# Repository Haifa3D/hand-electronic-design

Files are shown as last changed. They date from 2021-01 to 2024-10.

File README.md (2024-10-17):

# Oded Hand Electrical Design  

This project is a sub-project of Haifa3D Robotic Hand.
In this project, we present the electrical design of the Oded Hand – a 3D printed robotic hand with five micro-DC motors. 
The aim of this design is to be low cost, accessible, easy to assemble, robust and lightweight.  

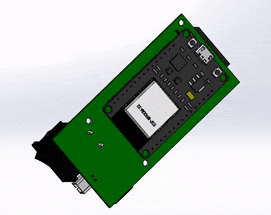
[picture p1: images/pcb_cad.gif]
   hand_gif  

## Design Description  
The Oded Hand can perform a variety of user-defined hand configurations using an autonomous adaptive grip along with a variety of configurable grip force levels.
The electrical design consists of four fingers with four different tendon-driven mechanisms actuated by four micro-DC motors, a passive thumb which magnetically locks in two discrete positions and wrist rotation driven by planetary gears and a DC motor. 

The electronic system consists of:
* The circuit and controller code
* The circuit housing and socket
* The batteries housing

The electronic system presented here also allows a Bluetooth communication between the Hand and your phone for settings configuration and a modular sensors control (see our [Mobile App](https://github.com/Haifa3D/haifa3d-hand-app)). For more details on how to manufacture and assemble the hand, please check out our [Mechanical Design](https://github.com/Haifa3D/hand-mechanical-design). 

## Who can benefit from this Design?  
The design is suitable for users with transradial amputation (below the elbow).
We welcome any new developers to enhance our design or to use the Oded Hand as a simulator for your new sensors/algorithms/methods that would potentially help users with controling their prosthetic hand.

## Design Files and Versions  
The STL files for the battery housing and the circuit housing can be found [here](CAD_files). The gerber files of the PCB design can be found [here](gerber_files/CAMOutputs) as well as the [schematic and layout](docs). The EAGLE files for modifying the board can be found [here](EAGLE_files). The Arduino code for the controller can be downloaded from [here](controller_software/Oded_Hand_board7_app2_4_6).

## Getting Started:
To build the electronic system for Oded Hand you will need a basic knowledge of soldering and the following componenets: 

| Component Name | Quantity | Value | links |
| --- | --- | --- | --- |
| ESP32 DEVKIT V1| 1 | - | [pinouts](https://randomnerdtutorials.com/esp32-pinout-reference-gpios/) [aliexpress](https://www.aliexpress.com/item/4000071762309.html?spm=a2g0s.9042311.0.0.64074c4du1Hh8a) |
| DRV8833 Pololu breakout board | 3 | - | [pololu](https://www.pololu.com/product/2130) | 
| micro metal dc motor | 5 | MP/LP, 100-200 RPM x 4, 30RPM x 1 | [pololu](https://www.pololu.com/product/2360), [aliexpress](https://www.aliexpress.com/item/1005003482247510.html?spm=a2g0o.productlist.main.5.70497ad7QQdXAy&algo_pvid=51493eeb-ec56-46bd-8e1c-2290c1519572&algo_exp_id=51493eeb-ec56-46bd-8e1c-2290c1519572-2&pdp_npi=3%40dis%21USD%212.08%211.44%21%21%21%21%21%40212279b716866852206383478d075c%2112000025985331271%21sea%21IL%211746261860&curPageLogUid=CFjbpVP4CzBR) | 
| IDC Connector flat cable | 1 x Right Angle Male + 1 x Female | 5x2 pins | [aliexpress RA Male](https://www.aliexpress.com/item/32841491672.html?spm=a2g0s.9042311.0.0.64074c4du1Hh8a), [aliexpress Female](https://www.aliexpress.com/item/32848157974.html?spm=a2g0s.9042311.0.0.64074c4du1Hh8a) |
| KF2510 Connector | 1 x Right Angle Male + 1 x Female  | 2 pins, 2.54mm pitch | [aliexpress](https://www.aliexpress.com/item/4000229650832.html?spm=a2g0o.productlist.0.0.580e59f7kz5W45&algo_pvid=70b8595e-d2a1-41e6-90ef-ca210f686aeb&algo_expid=70b8595e-d2a1-41e6-90ef-ca210f686aeb-20&btsid=2100bb4c16102253905804689e5410&ws_ab_test=searchweb0_0,searchweb201602_,searchweb201603_) |
| Right Angle SPDT Rocker Switch | 1 | for 3 Amp | [aliexpress](https://www.aliexpress.com/i/33009610601.html) |
| RGB LED Common Cathode | 1 | Common Cathode | [aliexpress](https://www.aliexpress.com/item/32666259962.html?spm=a2g0s.9042311.0.0.27424c4dhW29h7) |
| Li-ion 18650 battery | 2-4 | >2500mAh | [aliexpress](https://www.aliexpress.com/item/4000838767077.html?spm=a2g0o.detail.1000013.7.89c81382J9Ew7p&gps-id=pcDetailBottomMoreThisSeller&scm=1007.13339.291025.0&scm_id=1007.13339.291025.0&scm-url=1007.13339.291025.0&pvid=9ae560ff-e9e4-4dd9-a998-aac4cd26bcfe&_t=gps-id:pcDetailBottomMoreThisSeller,scm-url:1007.13339.291025.0,pvid:9ae560ff-e9e4-4dd9-a998-aac4cd26bcfe,tpp_buckets:668%232846%238116%232002&pdp_npi=3%40dis%21USD%213.75%212.62%21%21%21%21%21%402103244816864283632677463e15d8%2110000008755087021%21rec%21IL%211746261860) |
| battery Spring Contact Plate For AA AAA Battery | 4 | =< 12x12 mm |[aliexpress](https://www.aliexpress.com/item/1005001308633882.html?spm=a2g0o.detail.1000014.4.231d5d481DZZjH&gps-id=pcDetailBottomMoreOtherSeller&scm=1007.33416.205061.0&scm_id=1007.33416.205061.0&scm-url=1007.33416.205061.0&pvid=e82892c5-870e-4ffe-bb26-f0607f6946e2&_t=gps-id:pcDetailBottomMoreOtherSeller,scm-url:1007.33416.205061.0,pvid:e82892c5-870e-4ffe-bb26-f0607f6946e2,tpp_buckets:668%230%23131923%2347_668%23888%233325%235_23416%230%23205061%2320_23416%234721%2321967%23165_23416%234722%2321972%2310_668%232846%238112%231997_668%232717%237562%23468_668%231000022185%231000066059%230_668%233422%2315392%23668_4452%230%23211409%230_4452%233474%2315675%2389_4452%234862%2322449%23497_4452%233098%239599%23887_4452%235108%2323442%23113_4452%233564%2316062%236) |
| Resistors (through hole) |  | 1x2M, 1x1M, 1x10K, 2x100ohm, 1x150ohm, 5x(0.5-0.7)ohm | |

### Instructions
* send the [gerber files](gerber_files/CAMOutputs) for manufacturing at one of the availble online services (for instance, check out [PCBWay](https://www.pcbway.com/))

* order all the components from the list above.

* Cut the drv8833 according to [Pololu's instructions](https://www.pololu.com/product/2130) and check that both of the Isense pins are NOT grounded:
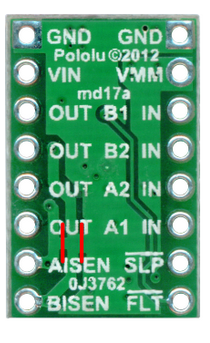
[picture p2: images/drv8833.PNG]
 
[image was taken from Pololu website]

*Tip: cut with a sharp knife the two lines, check with multimeter the resistence between AISEN/BISEN and GND. should be ~100Mohms*

* solder the headers of the drv8833 so the chip faces upward:
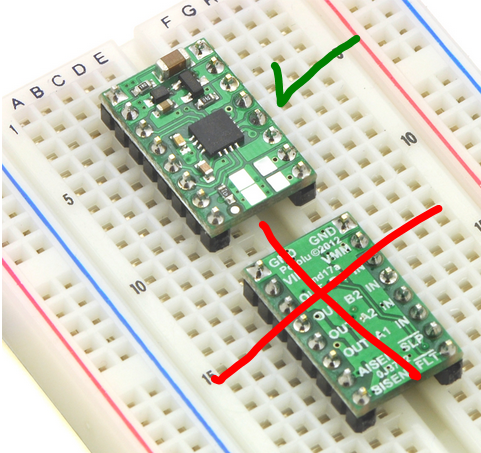
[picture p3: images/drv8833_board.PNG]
 
[image was taken from Pololu website]

* Solder the top side of the board (all components except the ESP32 and resistors)
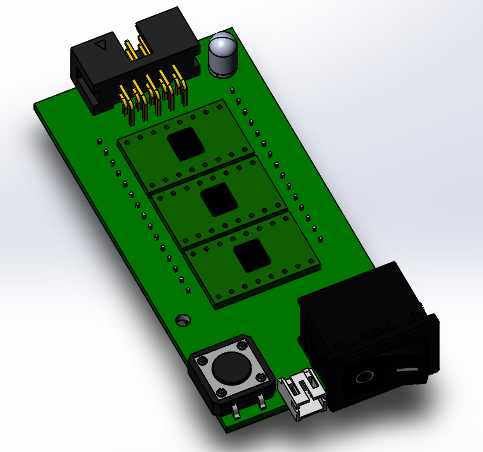
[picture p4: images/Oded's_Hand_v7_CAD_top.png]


*Tip: start from the led(the smallest pitch) --> drivers (drv8833)-->connectors --> button --> Switch

* Check all connections with a multimeter, to make sure everything was soldered correctly. Then cut all the pins so when you insert the esp32 controller to the bottom part nothing touches the controller. 

* Upload the [arduino code](controller_software/Oded_Hand_board7_app2_4_6) to the esp32 or an empty code, and only then solder the esp32 and the resistors (making sure there is no previous code that might cause problem to the component when it turned on). For the resistors: 1M and 2M for the voltage divider, 10K for the button, 2x100 and 1x150 ohm for the LEDs, 5x0.5ohm for the Rsense (you can use also 0.7 ohm)
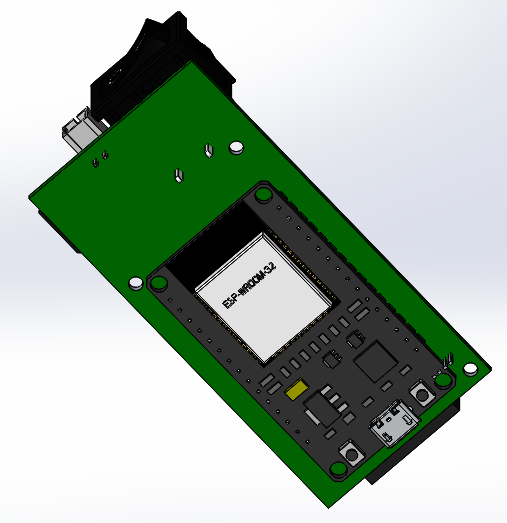
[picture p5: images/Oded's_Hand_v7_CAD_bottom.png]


After you complete the PCB assembly of Oded's Hand, please refer to the [Mechanical Design](https://github.com/Haifa3D/hand-mechanical-design) to assemble the mechanical parts of Oded's Hand. If you have already assembled the mechanical and the electrical parts, you are welcome to check out our [Mobile App](https://github.com/Haifa3D/haifa3d-hand-app) to refine the controller parameters and to define your favorite hand movements.

### **If it is the first time you are using the controller - download our [Mobile App](https://play.google.com/store/apps/details?id=com.gjung.haifa3d), connect to the hand, go to configuration and click on RESET Configuration and RESET Presets before any other action.**

## The Controller Software (Arduino code):
The code can be found [here](controller_software/Oded_Hand_board7_app2_4_6)

All installation instruction can be found in the code.

In general:

*working with Arduino IDE on ESP32:*

*https://randomnerdtutorials.com/installing-the-esp32-board-in-arduino-ide-windows-instructions/*

*Board Manager: esp32 by Espressif Systems 1.0.6~*

*Arduino IDE supported version ~1.8.15*

*install the following libraries:*

*ESP32 AnalogWrite by ERROUAGUY 0.1.0*

*ESP32 BLE Arduino Kolban/Krempa 1.0.1*

## The Circuit Housing and Socket
[Here](hand-electronic-design/CAD_files/circuit_housing), you can find the CAD of the circuit itself, the housing of the circuit top and bottom parts and the socket design we are using.
The socket is basically a flat surface which can be thermoformed and adjusted to fit the user arm. Usually the important measurements are the perimeter and length of the user's arm.

*Recommendation, merge the bottom part of the circuit housing into your socket design and print it as one part. If your socket design is based on thermoforming, heat the inner part of the socket so the bottom part of the circuit housing will not get deformed*.

To assemble the circuit housing you will need **3 x M2.5 5-8mm self tap screws** to mount the PCB to the bottom part and **2 x M2 5-6mm self tap screws** to connect the top to the bottom. To connect the hand to the socket you can use **3 x M2.5 5-8mm self tap screws** as well.

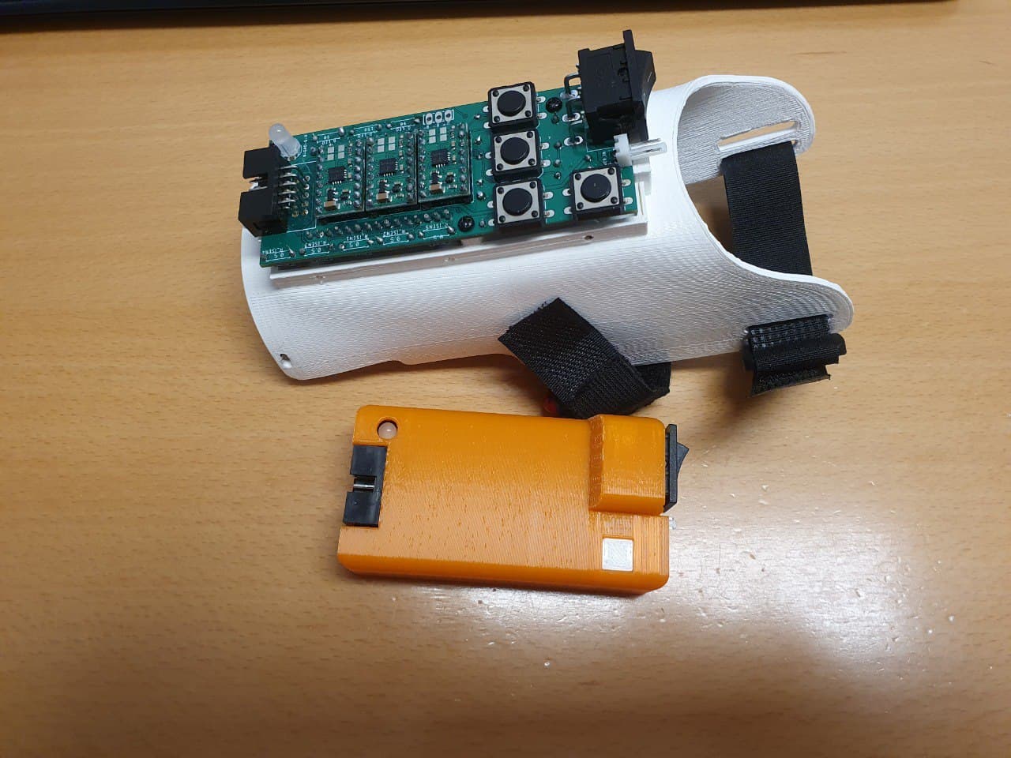
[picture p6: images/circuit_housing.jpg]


*The pictured circuit on the socket is from a previous version where we had 3 buttons on the hand instead of the mobile app for control.*

## The Batteries Housing
You can use any two connected batteries in series to power the circuit. 
To assemble your own battery pack:
* print the [batteries housing files](CAD_files/batteries_housing) (*Notice the printing orientation - the 'battery_top' should be printed so its snap is parallel to the ground*)
* make sure the batteries can slide in smoothly without getting stuck at the housing walls.
* Solder the battery Spring Contact Plate - at the 'battery-top' (the lid) the plates should be soldered to each other and at the bottom each plate should be soldered to a different wire (the maximal total current can be 2.5 amp so make sure you select a suitible wire)
* Insert the filaments to mount the contact plates to the rectangular slots at the top and bottom parts. Make sure the plates are not touching each other at the bottom part (otherwise you are going to short the batteries).
* cut the excess filaments and heat the ends (see the yellow fillaments in the image below)
* screw the bottom part to the body using two **M2 4-5mm self tap screws**
* check the connection and add a 2PIN Female KF2510 Connector to the wires.
* cut an elastic strap and sew velcro (or just buy a suitible velcro elatic strap) to fasten the Battery Pack to your upper arm. a design for backles and rings are also available at the same folder.

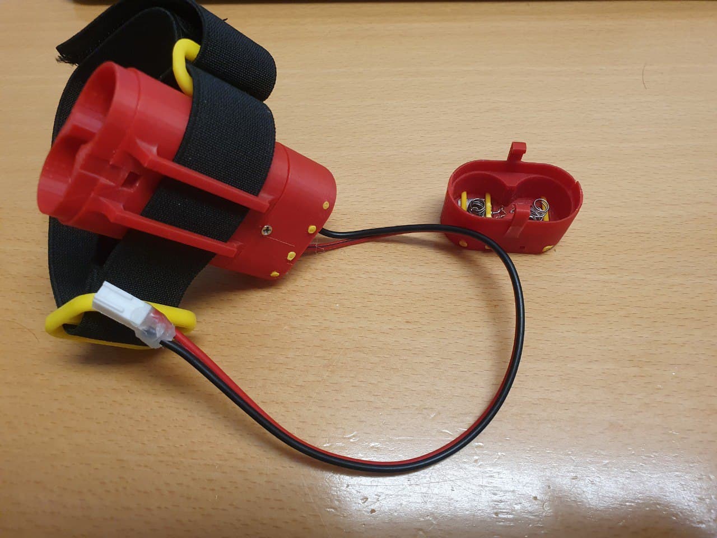
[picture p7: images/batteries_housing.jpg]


## So What To Do Next?
If you have developed a user interface for prosthetic hands and want to implement it on a low-cost prosthetic hand, you can communicate with our Hand in three different ways:
* if your sensors and system are on the hand and arm - you can implement your code to our controller code and solder your system to the free pins (GPIO2,12,25)
* if your system is android-based - use our [**mobile app and SDK**](https://github.com/Haifa3D/haifa3d-hand-app) to wirelessly communicate with our Hand 
* if your system is esp32-based - use the example Arduino IDE code [here](controller_software/Hand_UI_demo_BLEclient) to communicate with our Hand using the built-in BLE of the esp32 controller.
* if your system is based on Python code - use the [communication example Python code](python_communication_code/) to trigger different hand movements

## Acknowledgements:
This project was done by a group of great people and with the help and guidance of generous organizations.

*Electrical design*:  Shunit Polinsky, Yair Herbest, and Noah Bernten.

*Users Communication*: Haifa 3D – a nonprofit organization that designs and builds hands for free, founded by Yoav Medan and Yacov Malinovich.

*Resources*: The Technion - Israel Institute of Technology and special thanks to Prof. Alon Wolf and the Biorobotics and Biomechanics Lab.

## Donation:


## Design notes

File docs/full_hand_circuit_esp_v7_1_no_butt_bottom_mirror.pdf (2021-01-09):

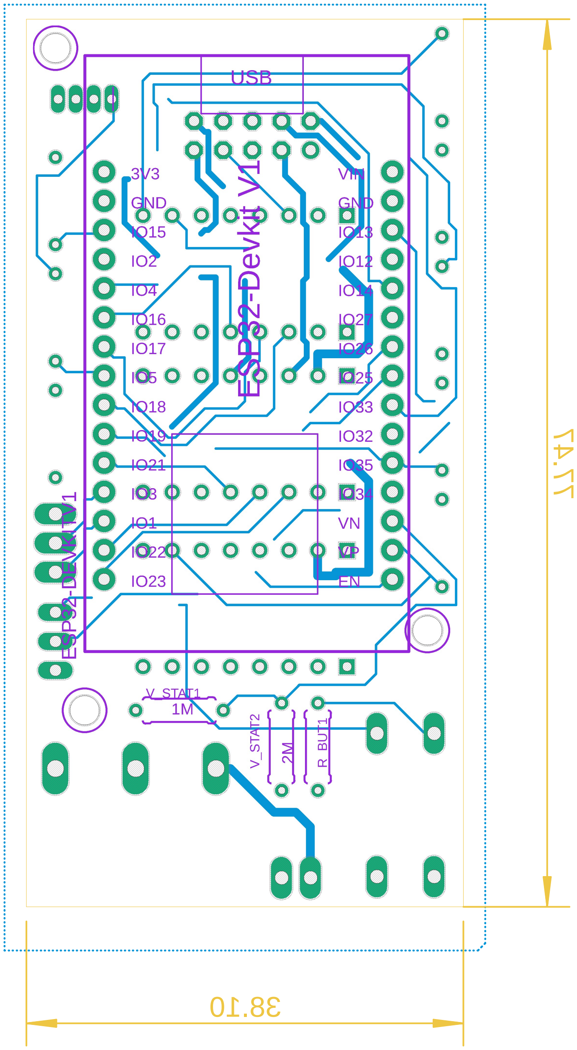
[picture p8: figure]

09-Jan-21 18:08 f=2.00 mirrored C:\Users\Lenovo\Documents\EAGLE\projects\Oded's Hand v7\full_hand_circuit_esp_v7_1_no_butt.brd

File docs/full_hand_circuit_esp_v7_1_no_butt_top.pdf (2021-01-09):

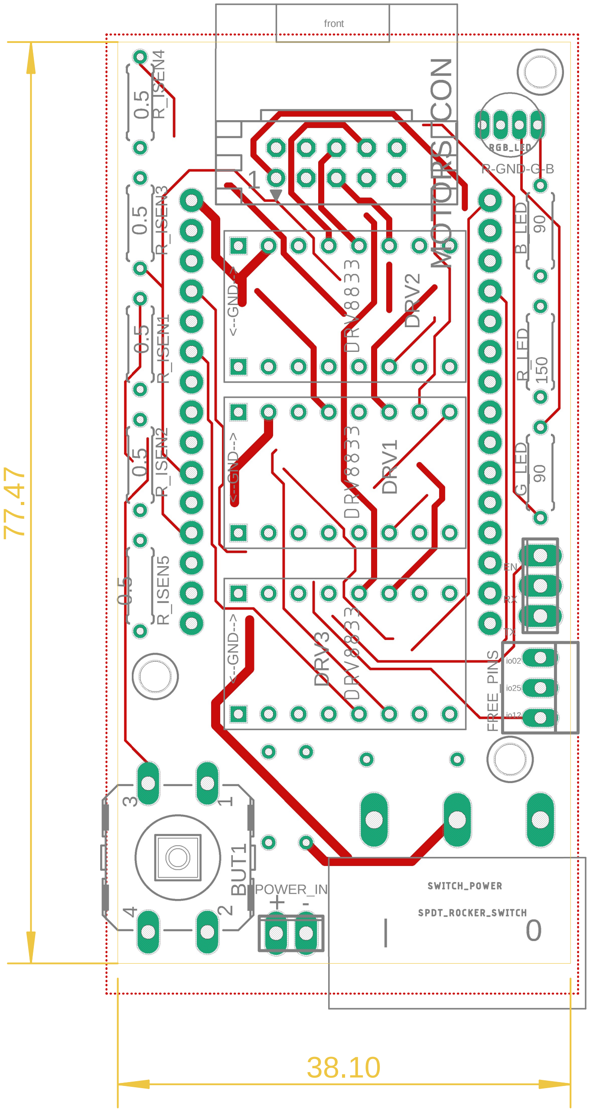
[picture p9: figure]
front

09-Jan-21 18:08 f=2.00 C:\Users\Lenovo\Documents\EAGLE\projects\Oded's Hand v7\full_hand_circuit_esp_v7_1_no_butt.brd

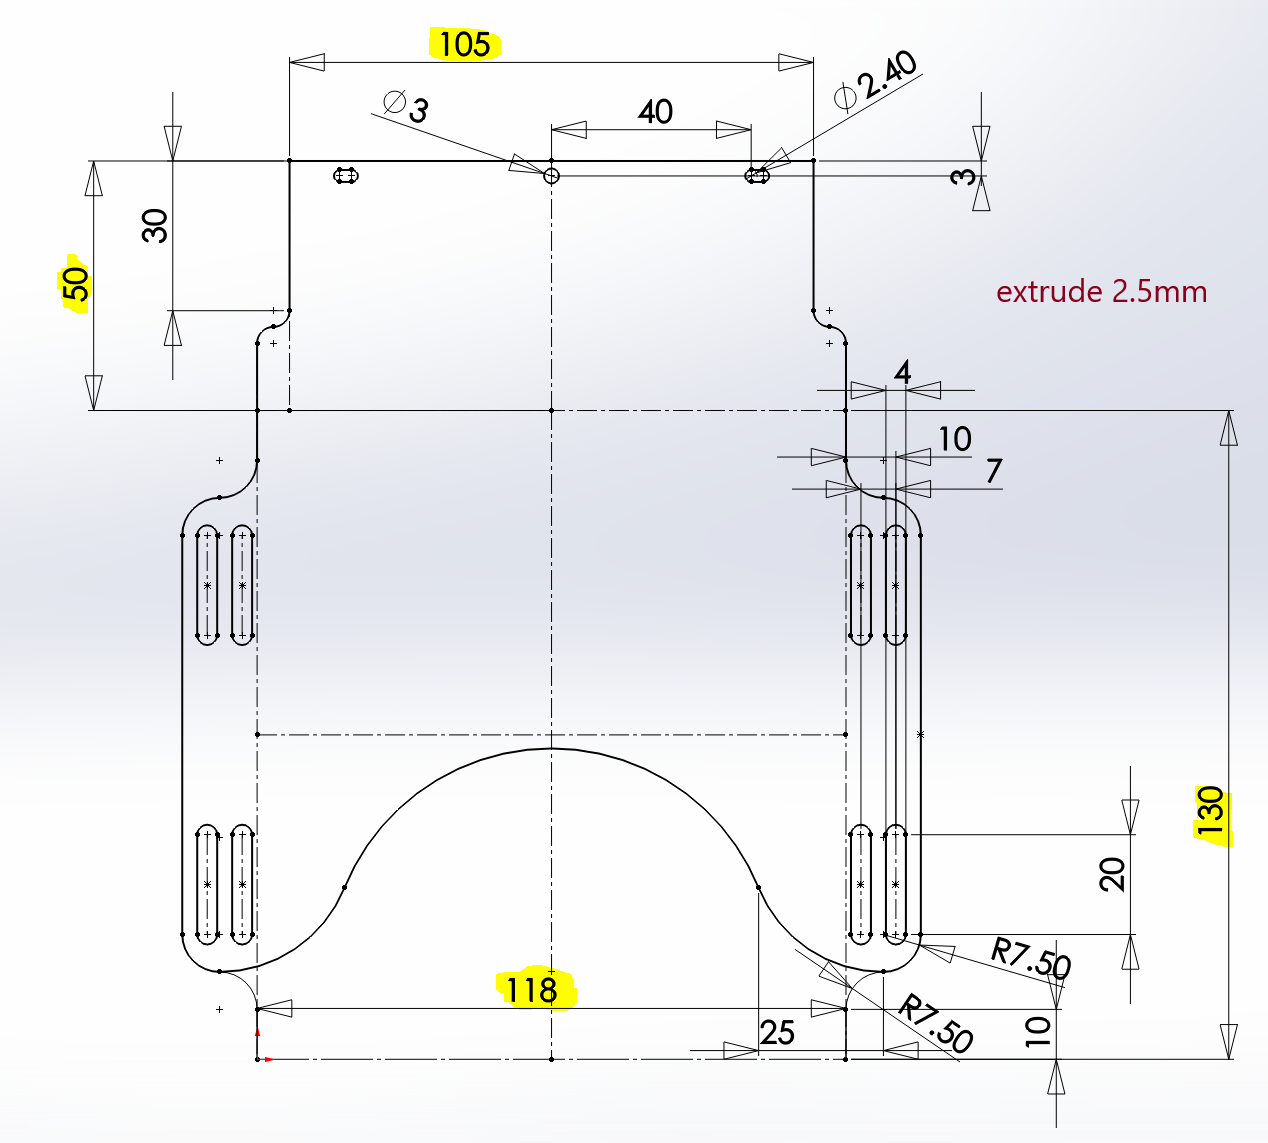
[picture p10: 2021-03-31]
CAD_files/circuit_housing/socket_sketch.PNG

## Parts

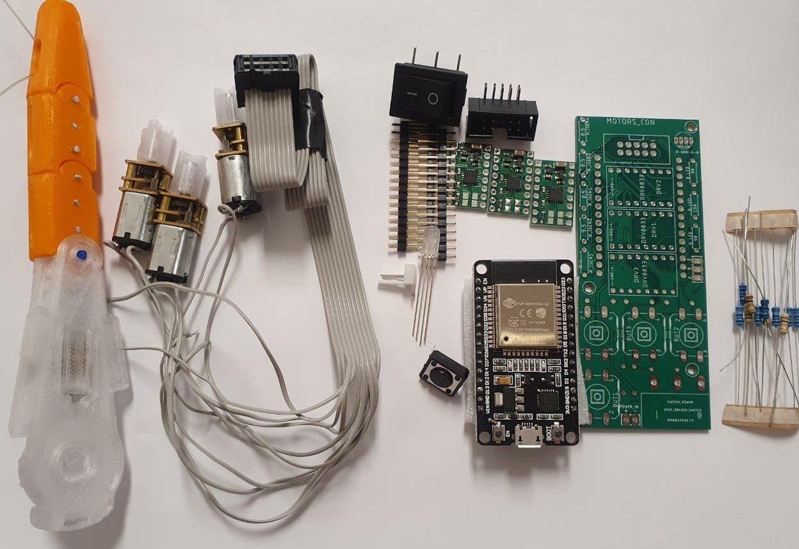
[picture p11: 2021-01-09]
images/full_electronic_component_v7.jpg

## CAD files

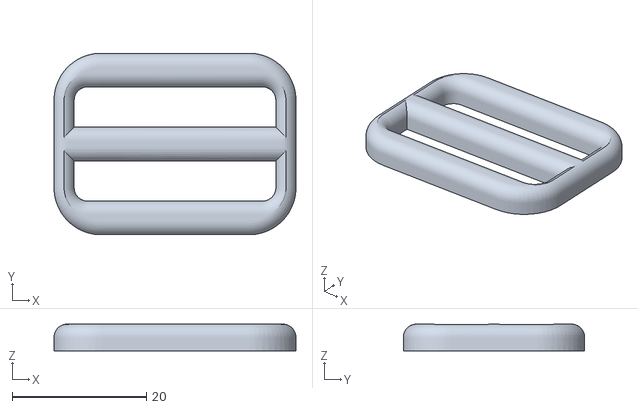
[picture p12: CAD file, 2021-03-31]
CAD_files/batteries_housing/battery_pack_25mm_strap_buckle.STL
36.0 x 27.0 x 4.00

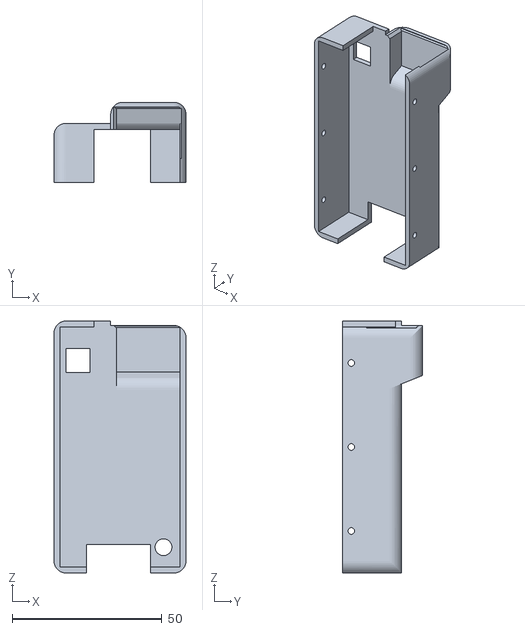
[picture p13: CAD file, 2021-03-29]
CAD_files/circuit_housing/circuit_v7_top.STL
44.0 x 26.8 x 84.0

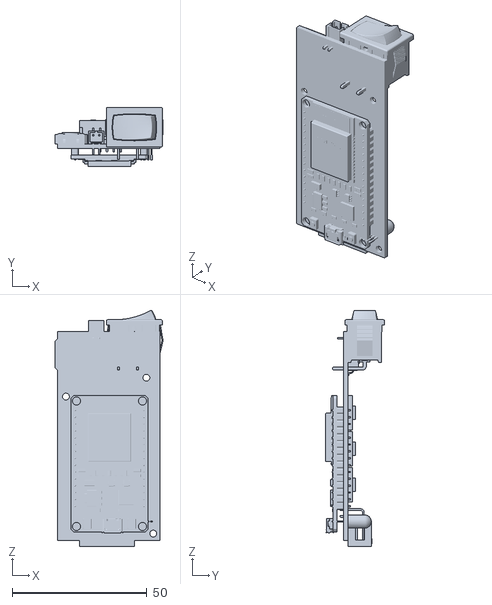
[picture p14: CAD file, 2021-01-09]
CAD_files/circuit_housing/pcb-not_for_print/circuit7.STL
40.1 x 22.0 x 87.5

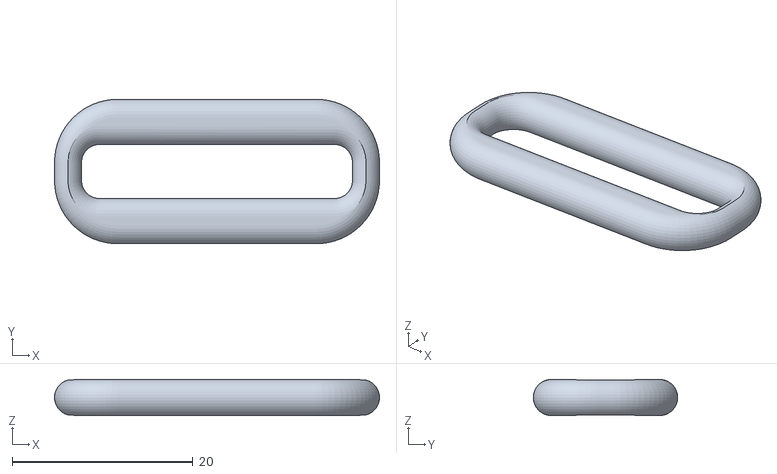
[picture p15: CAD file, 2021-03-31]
CAD_files/batteries_housing/battery_pack_25mm_strap_ring.STL
36.0 x 16.0 x 4.00

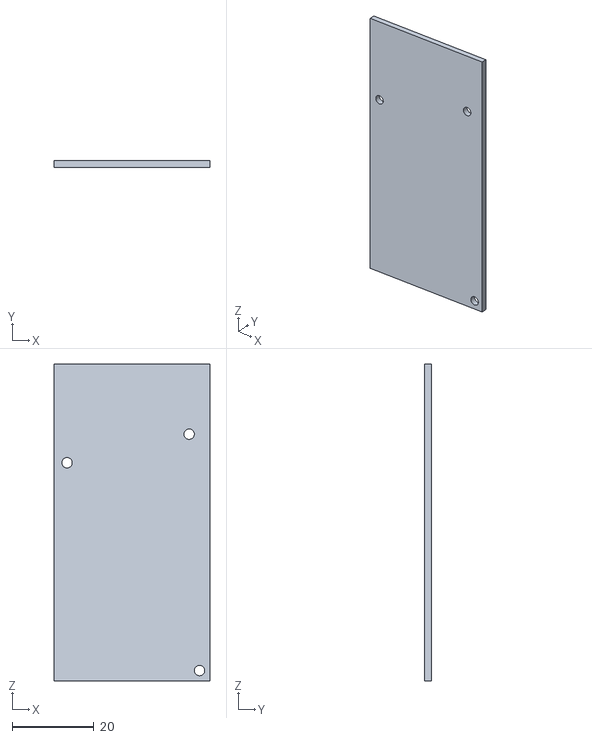
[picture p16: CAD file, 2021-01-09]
CAD_files/circuit_housing/pcb-not_for_print/pcb7.STL
38.1 x 1.60 x 77.5

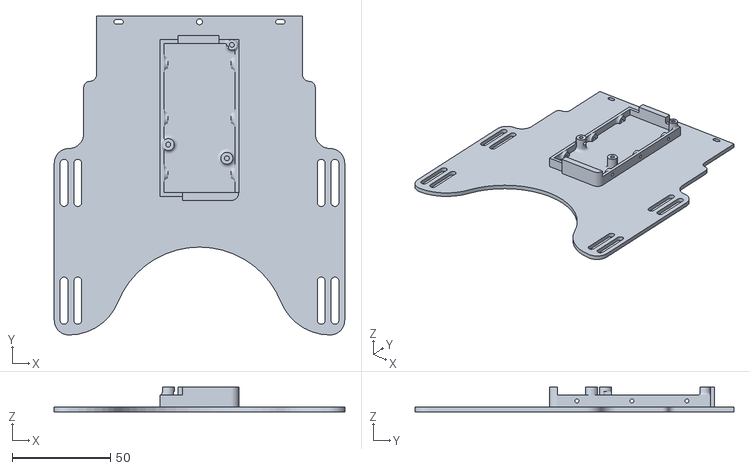
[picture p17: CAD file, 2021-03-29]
CAD_files/circuit_housing/socket_with_circuit_v7_bottom.STL
148.0 x 162.5 x 12.5

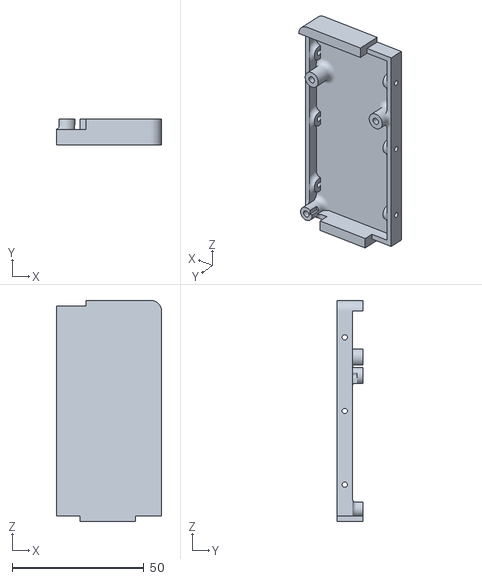
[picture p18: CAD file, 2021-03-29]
CAD_files/circuit_housing/circuit_v7_bottom.STL
40.0 x 10.0 x 84.0

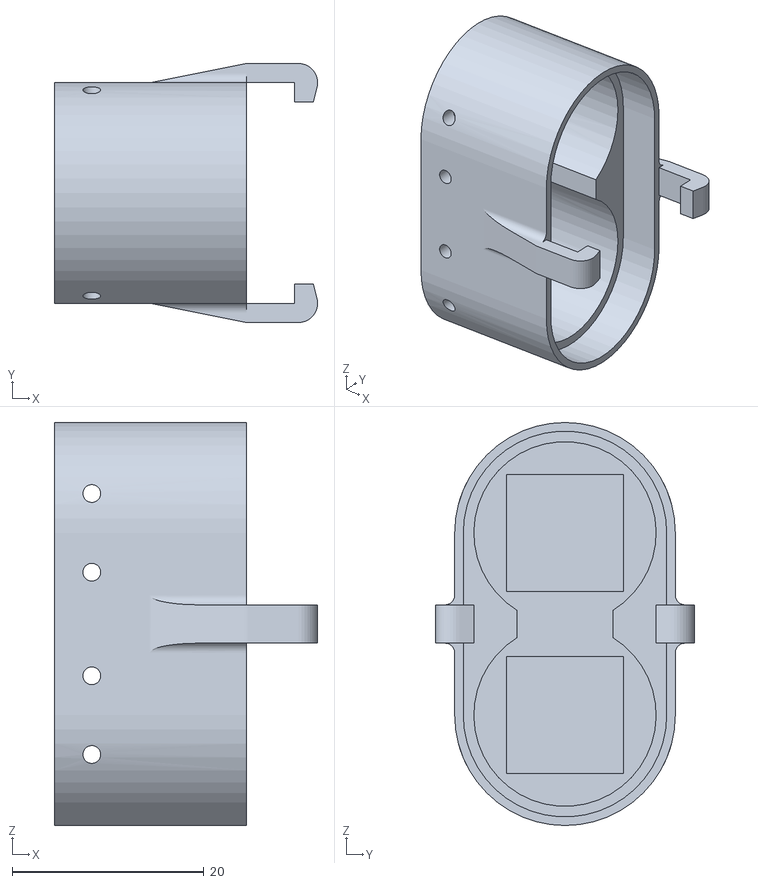
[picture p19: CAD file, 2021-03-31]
CAD_files/batteries_housing/battery_top.STL
27.4 x 27.0 x 42.0

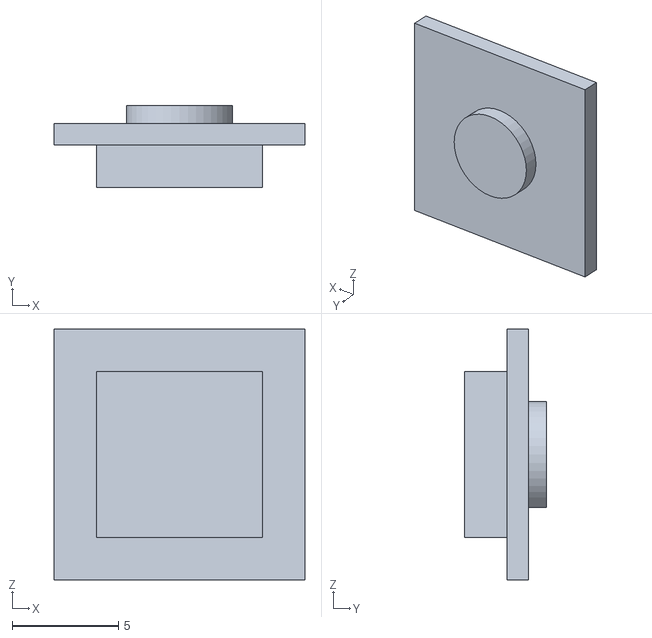
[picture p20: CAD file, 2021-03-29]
CAD_files/circuit_housing/button.STL
11.8 x 3.85 x 11.8

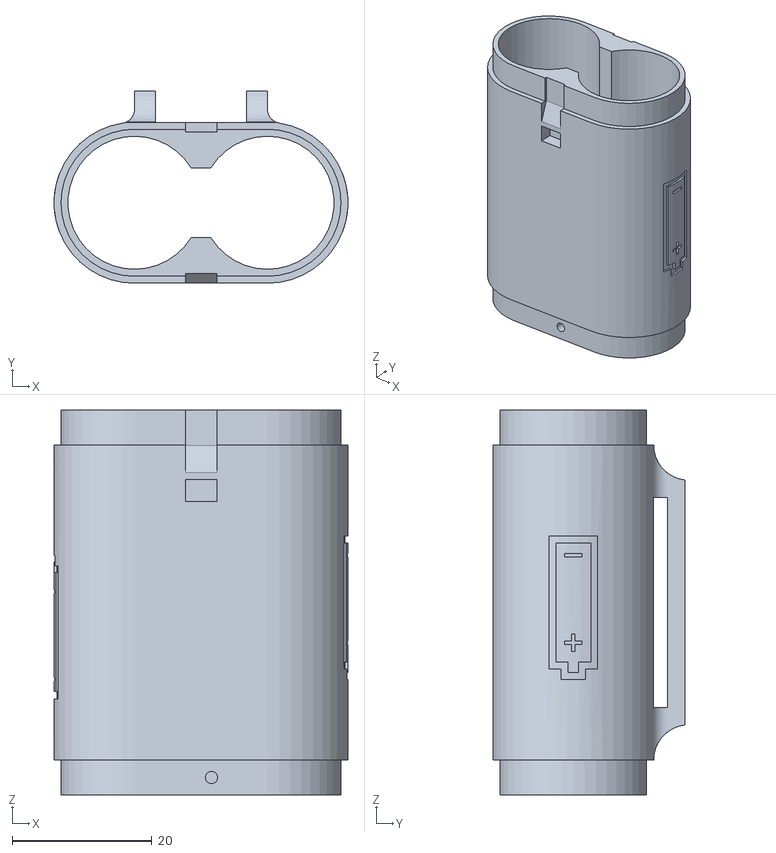
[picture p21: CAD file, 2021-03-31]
CAD_files/batteries_housing/battery_body.STL
42.0 x 27.5 x 55.0

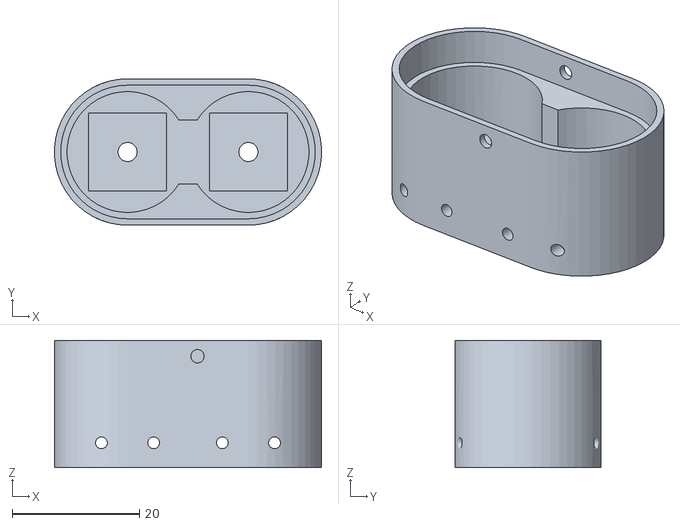
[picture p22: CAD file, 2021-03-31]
CAD_files/batteries_housing/battery_bottom_screw.STL
42.0 x 23.0 x 20.0

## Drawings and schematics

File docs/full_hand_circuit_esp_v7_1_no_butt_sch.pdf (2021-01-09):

## Driving System block

## Controller Block

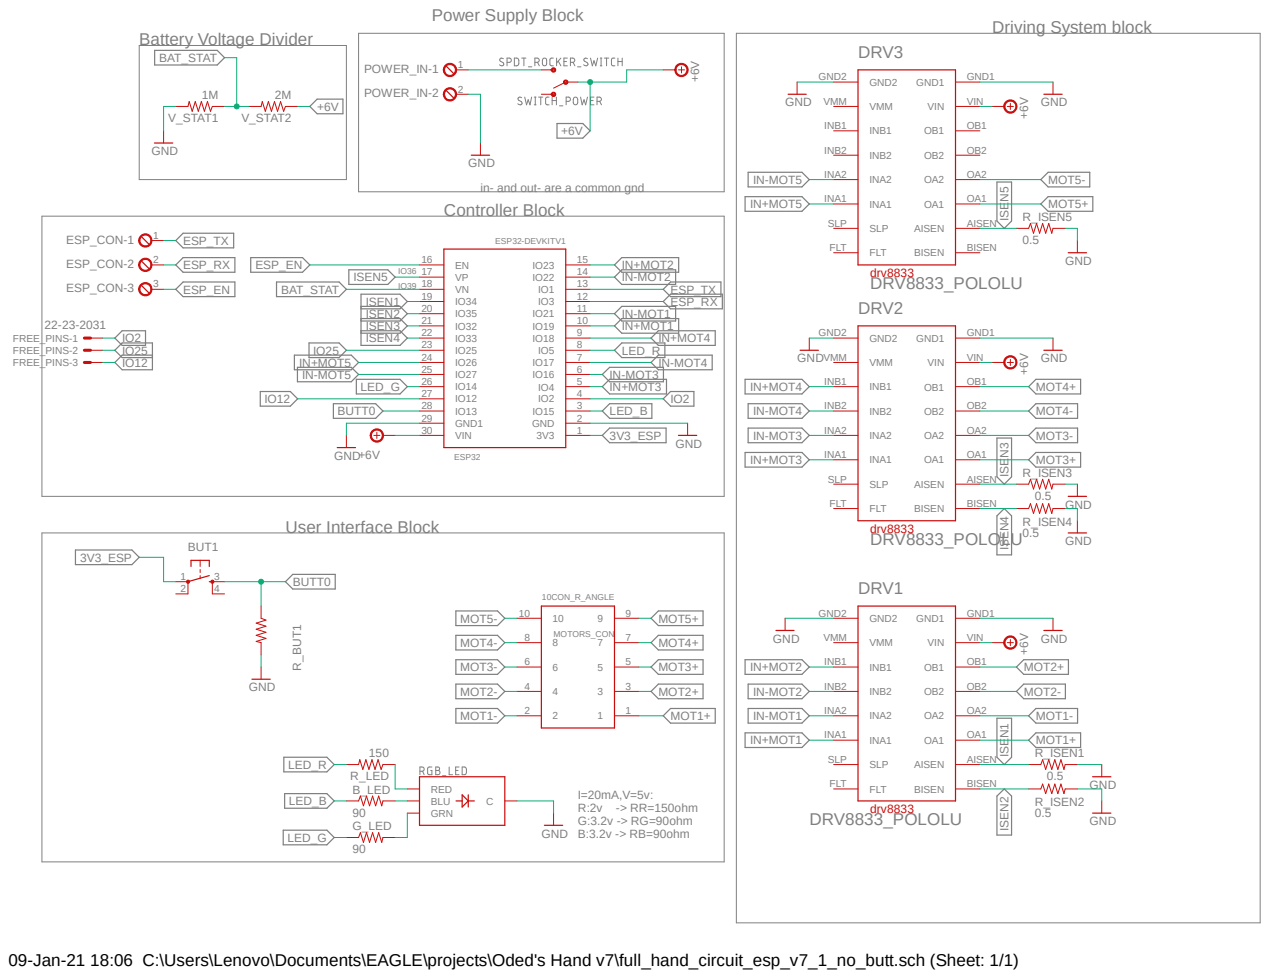
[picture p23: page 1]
I=20mA,V=5v: R:2v -> RR=150ohm G:3.2v -> RG=90ohm B:3.2v -> RB=90ohm; DRV8833_POLOLU; GND; 10CON_R_ANGLE; ESP32-DEVKITV1; 0.5 GND; FLT FLT; SLP SLP; INA1 INA1; INA2 INA2; INB2 INB2; INB1 INB1; VMM VMM; GND2 GND2; BISEN; AISEN; VIN; GND1; GND1 DRV1; GND1 DRV2; GND1 DRV3; MOTORS_CON; GRN; BLU; C B_LED; RED R_LED; G_LED; 1 ESP_CON-1; 2 ESP_CON-2; 3 ESP_CON-3; VP 17 VN 18 IO34 19 IO35 20 IO32 21 IO33 22 IO25 23 IO26 24 IO27 25 IO14 26 IO12 27 IO13 28 GND1 29 VIN 30; ESP32; V_STAT1; V_STAT2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

Power Supply Block

Battery Voltage Divider
BAT_STAT

GND
in- and out- are a common gnd

User Interface Block

09-Jan-21 18:06 C:\Users\Lenovo\Documents\EAGLE\projects\Oded's Hand v7\full_hand_circuit_esp_v7_1_no_butt.sch (Sheet: 1/1)

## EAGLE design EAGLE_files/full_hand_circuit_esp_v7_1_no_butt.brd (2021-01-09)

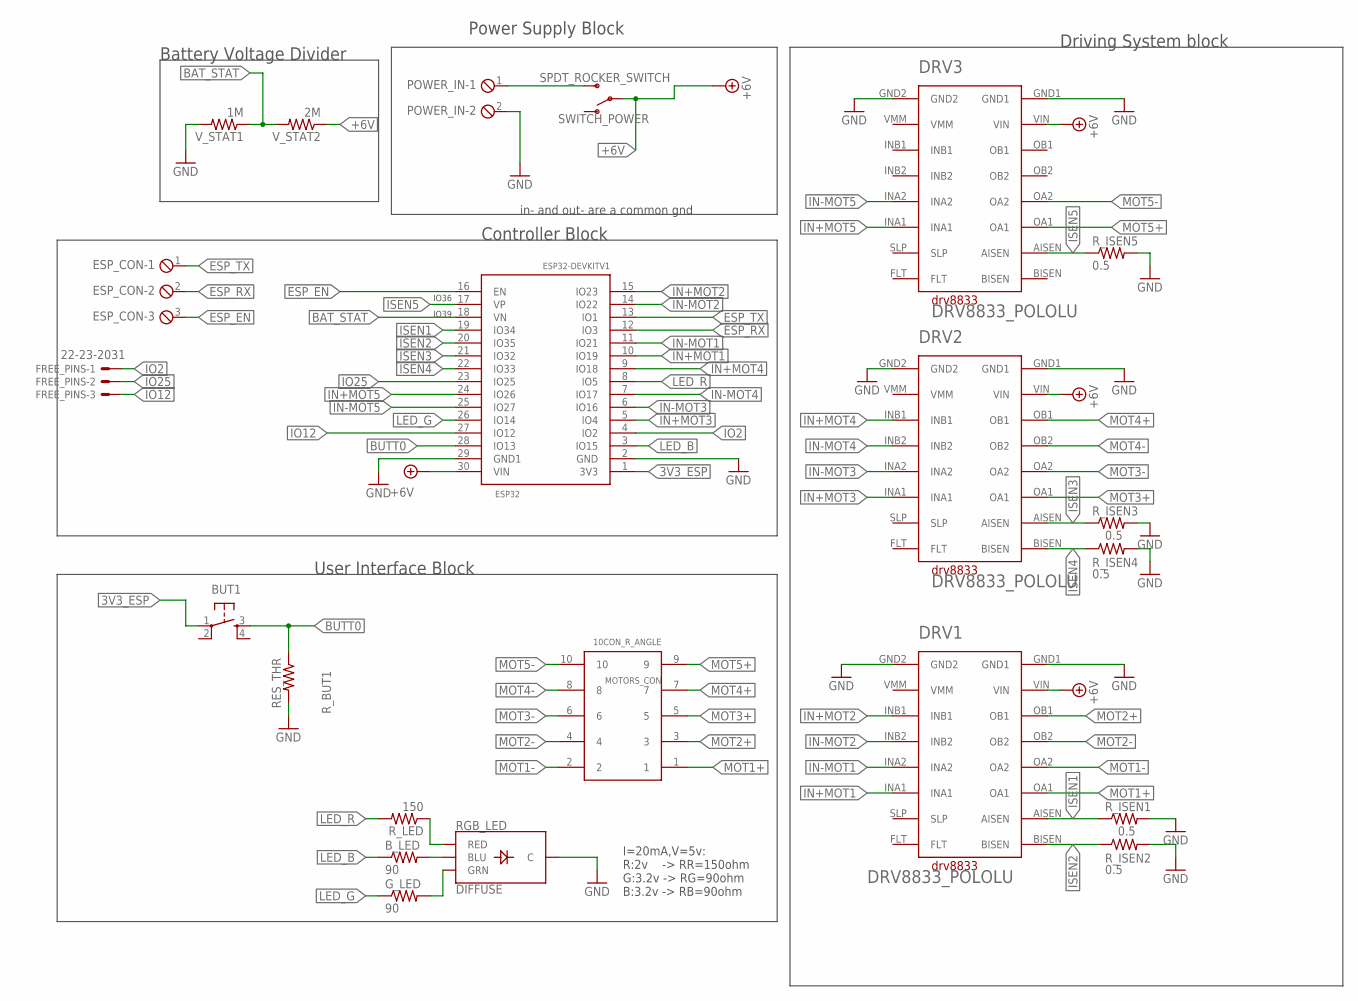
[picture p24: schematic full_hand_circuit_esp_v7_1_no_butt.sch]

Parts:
BUT1: PUSH_BUTTON; B3F-40XX
B_LED: 90; R_THR
DRV1, DRV2, DRV3: DRV8833_POLOLU
ESP32: ESP32DEVKITV1; ESP32-DEVKITV1
ESP_CON: MPT3; 3POL254
FREE_PINS: 22-23-2031
G_LED: 90; R_THR
MOTORS_CON: 10CON_R_ANGLE; CON10_R_ANGLE
POWER_IN: MPT2; 2POL254
RGB_LED: DIFFUSE; LED-RGB-THRU
R_BUT1: RES_THR; R_THR
R_ISEN1, R_ISEN2, R_ISEN3, R_ISEN4, R_ISEN5: 0.5; R_THR
R_LED: 150; R_THR
SWITCH_POWER: SPDT_ROCKER_SWITCH; SWITCH_SPDT_PTH_11.6X4.0MM
V_STAT1: 1M; R_THR
V_STAT2: 2M; R_THR

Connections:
3V3_ESP: BUT1.1, ESP32.1 (3V3)
+6V: DRV1.VIN, DRV2.VIN, DRV3.VIN, ESP32.30 (VIN), SWITCH_POWER.2, V_STAT2.1
BAT_STAT: ESP32.18 (VN), V_STAT1.1, V_STAT2.2
BLUE: B_LED.2, RGB_LED.4 (BLU)
BUTT0: BUT1.3 (S), ESP32.28 (IO13), R_BUT1.1
ESP_EN: ESP32.16 (EN), ESP_CON.3
ESP_RX: ESP32.12 (IO3), ESP_CON.2
ESP_TX: ESP32.13 (IO1), ESP_CON.1
GND: DRV1.GND1, DRV1.GND2, DRV2.GND1, DRV2.GND2, DRV3.GND1, DRV3.GND2, ESP32.2 (GND), ESP32.29 (GND1), POWER_IN.2, RGB_LED.2 (C), R_BUT1.2, R_ISEN1.2, R_ISEN2.2, R_ISEN3.2, R_ISEN4.2, R_ISEN5.2, V_STAT1.2
GREEN: G_LED.2, RGB_LED.3 (GRN)
IN+MOT1: DRV1.INA1, ESP32.10 (IO19)
IN+MOT2: DRV1.INB1, ESP32.15 (IO23)
IN+MOT3: DRV2.INA1, ESP32.5 (IO4)
IN+MOT4: DRV2.INB1, ESP32.9 (IO18)
IN+MOT5: DRV3.INA1, ESP32.24 (IO26)
IN-MOT1: DRV1.INA2, ESP32.11 (IO21)
IN-MOT2: DRV1.INB2, ESP32.14 (IO22)
IN-MOT3: DRV2.INA2, ESP32.6 (IO16)
IN-MOT4: DRV2.INB2, ESP32.7 (IO17)
IN-MOT5: DRV3.INA2, ESP32.25 (IO27)
IN_HIGH: POWER_IN.1, SWITCH_POWER.3 (S)
IO2: ESP32.4 (IO2), FREE_PINS.1
IO12: ESP32.27 (IO12), FREE_PINS.3
IO25: ESP32.23 (IO25), FREE_PINS.2
ISEN1: DRV1.AISEN, ESP32.19 (IO34), R_ISEN1.1
ISEN2: DRV1.BISEN, ESP32.20 (IO35), R_ISEN2.1
ISEN3: DRV2.AISEN, ESP32.21 (IO32), R_ISEN3.1
ISEN4: DRV2.BISEN, ESP32.22 (IO33), R_ISEN4.1
ISEN5: DRV3.AISEN, ESP32.17 (VP), R_ISEN5.1
LED_B: B_LED.1, ESP32.3 (IO15)
LED_G: ESP32.26 (IO14), G_LED.1
LED_R: ESP32.8 (IO5), R_LED.2
MOT1+: DRV1.OA1, MOTORS_CON.1
MOT1-: DRV1.OA2, MOTORS_CON.2
MOT2+: DRV1.OB1, MOTORS_CON.3
MOT2-: DRV1.OB2, MOTORS_CON.4
MOT3+: DRV2.OA1, MOTORS_CON.5
MOT3-: DRV2.OA2, MOTORS_CON.6
MOT4+: DRV2.OB1, MOTORS_CON.7
MOT4-: DRV2.OB2, MOTORS_CON.8
MOT5+: DRV3.OA1, MOTORS_CON.9
MOT5-: DRV3.OA2, MOTORS_CON.10
RED: RGB_LED.1 (RED), R_LED.1

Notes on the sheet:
Driving System block
I=20mA,V=5v: R:2v -> RR=150ohm G:3.2v -> RG=90ohm B:3.2v -> RB=90ohm
Controller Block
IO36
IO39
Power Supply Block
in- and out- are a common gnd
User Interface Block
Battery Voltage Divider

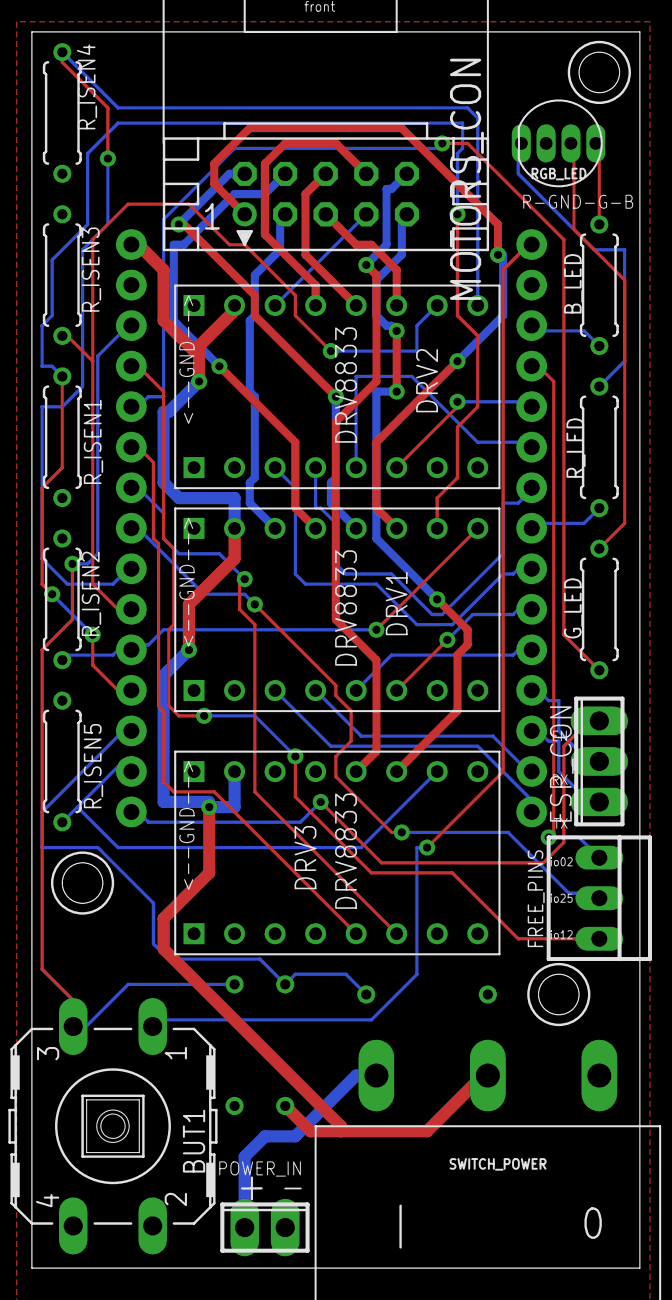
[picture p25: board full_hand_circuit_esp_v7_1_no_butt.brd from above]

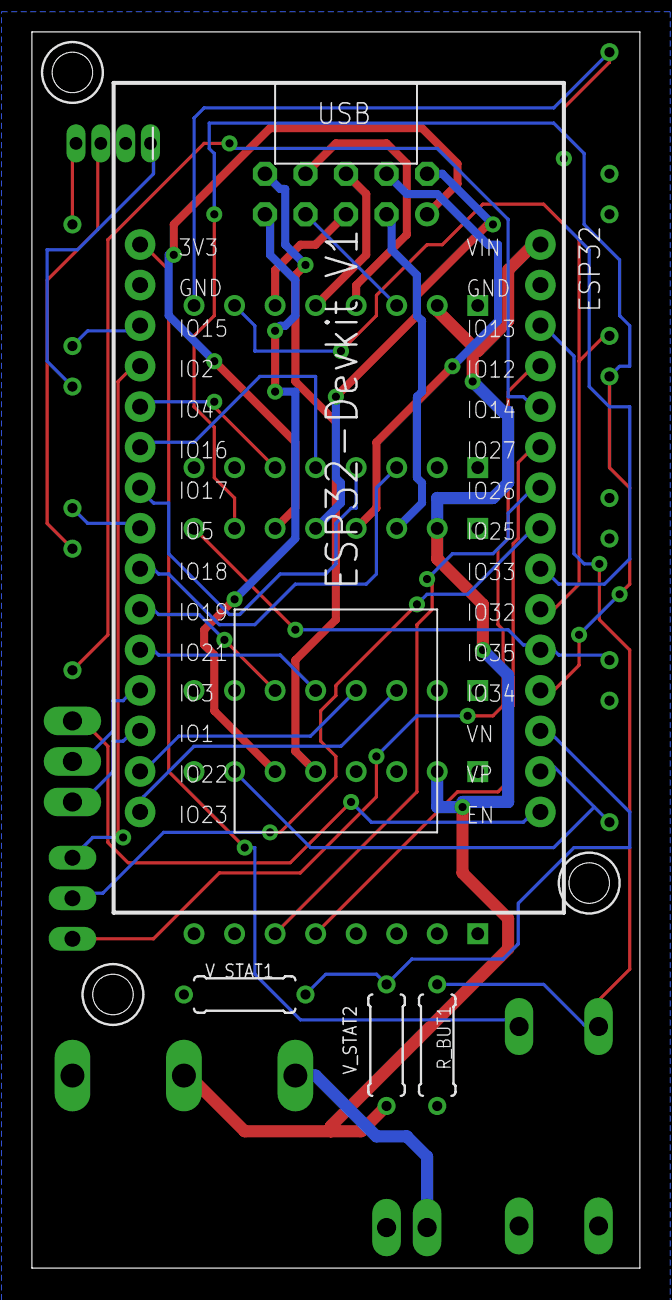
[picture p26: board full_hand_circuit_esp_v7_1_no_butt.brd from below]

Board: 2 copper layers, 38.1 x 77.5 mm, 22 parts (4 on the bottom side), 43 nets.

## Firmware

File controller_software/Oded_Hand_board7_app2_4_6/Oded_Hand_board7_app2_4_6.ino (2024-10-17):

/*
 * This code allows you to control the Oded Hand - a low cost, open source prosthetic hand that anyone can build
 * 
 * working with Arduino IDE on ESP32:
 * https://randomnerdtutorials.com/installing-the-esp32-board-in-arduino-ide-windows-instructions/
 * Board Manager:
 * esp32 by Espressif Systems 1.0.6~
 *
 * Libraries installation:
 * go to tools > manage Libraries...
 * install the following libraries:
 * ESP32 AnalogWrite by ERROUAGUY 0.1.0
 * ESP32 BLE Arduino Kolban/Krempa 1.0.1
 *
 * Arduino IDE supported version ~1.8.15
 *
 * The event holder here assigns tasks for each event. The structures is as follow:
 * task_type 0   :   do nothing
 * task_type 1   :   do action according to preset data
 * task_type 2   :   save new preset according to preset data
 * task_type 3   :   save new config according to config id
 * 
 * For more information about the BLE protocol see https://github.com/Haifa3D/haifa3d-hand-app/blob/master/Protocol.md
 * For more information about the Hardware, circuit and wiring see https://github.com/Haifa3D/hand-electronic-design
 * 
 * If you see the battery status is not correct go to the buttery function parameters and change the min and max value.
 * If you want to check the battery status faster, go to the Software setting, battery function
 * If you want to add/reduce number of buttons add at the Hardware button sections.
 * If you want to change the Button long click time, change the DT_LONG_CLICK
 * If you see the motors are not moving correctly (moving in the reversed directions or wrong motor is moving, go to Hardware motor connection
 * 
 */

/***********************************************************/
/*                Libraries                                */
/***********************************************************/
#include <Arduino.h>
#include <BLEDevice.h>
#include <BLEUtils.h>
#include <BLEServer.h> //Library to use BLE as server
#include <BLE2902.h> 
#include <bitset>
#include <EEPROM.h> // for ESP32 flash memory
#include <analogWrite.h> //PWM options

/*************************************************************************************/
/*                BlE Parameters and General Setting:                                */
/*************************************************************************************/
#define PRESETS_NUM 12  // number of presets, save on the ocntroller
#define CONFIG_NUM 13  //number of config parameters, save on the controller
#define CONFIG_TRIG_NUM 2  // number of config trigger, excute action without saving data on the controller
#define MAX_MOV 10  //maximal movements per presents, decided due to the limited amount of flsuh memory
#define ACTION_BYTES 4  // number of byte per action
#define MIN_PRESET_BYTES (1+ACTION_BYTES)  //one movements per preset
#define MAX_PRESET_BYTES (1+(MAX_MOV*ACTION_BYTES))  //MAX_MOV movements per preset
#define CONFIG_BYTES 20  // maximal number of config bytes. currently we utilized 13 config paramerters each param is 1 byte.
#define EEPROM_SIZE 512  // number of bytes we'll need to access in the flash memory. each char is 1 byte
#define TIME_UNITS 50  //one time units equals to TIME_UNITS[msec]
#define MOTORS_NUM 5  // number of motors connected to the hand

/*************************************************************************************/
/*                          HardWare Setting:                                        */
/*************************************************************************************/
// motors Connection - change between IN1 and IN2 if the motor moves at the reverse direction 
// and change between groups (each group consists of 3 values: IN1, IN2, ISENSE) if the wrong motor is moving.
#define W_IN1     26 
#define W_IN2     27 
#define W_ISENSE  36 

#define F1_IN1    19 
#define F1_IN2    21 
#define F1_ISENSE 34 

#define F2_IN1    23 
#define F2_IN2    22 
#define F2_ISENSE 35 

#define F3_IN1    4  
#define F3_IN2    16 
#define F3_ISENSE 32 

#define F4_IN1    18 
#define F4_IN2    17 
#define F4_ISENSE 33 

const int all_motors[MOTORS_NUM*2]={W_IN1,W_IN2,F1_IN1,F1_IN2,F2_IN1,F2_IN2,F3_IN1,F3_IN2,F4_IN1,F4_IN2};
const int all_controls[MOTORS_NUM*2]={W_ISENSE,F1_ISENSE,F2_ISENSE,F3_ISENSE,F4_ISENSE};

#define MODES_NUM 4 // 0 = long click modes, 1 = mode1, ..., currently we have 4 mode
#define MOV_PER_MODE 3  //currnely we have 3 movements per mode, total of 12 presets
#define BUTTONS_NUM 1  // depends on the circuit version, here we have only one button connected

#define BUTTON_MODE 13 //mode button
//#define BUTTON1     2  // button of movement 1
//#define BUTTON2     25  // button of movement 1
//#define BUTTON3     12 // button of movement 1
const int all_buttons[BUTTONS_NUM] = {BUTTON_MODE}; //{BUTTON_MODE, BUTTON1,BUTTON2,BUTTON3};

#define LEDS_NUM 3  //RGB led

#define LED1 5 //Red
#define LED2 14 //Green
#define LED3 15 //Blue
const int all_leds[LEDS_NUM] = {LED1,LED2,LED3};

const int battery_pin = 39; //GPIO 39 is connected to the 18650 Li-Ion battery with a voltage devider 1/3*Vin
 
/*************************************************************************************/
/*                          SoftWare Setting:                                        */
/*************************************************************************************/
// moving average
#define MAX_WINDOW 20  //the maximsl length of the smoothing window

// setting PWM properties for the leds
const int freq = 5000;  //[Hz]
const int resolution = 8;  //[bits] value is from 0 to 255

// buttons function - parameters and declaration:
#define DT_LONG_CLICK 1000  //[msec] the threshold time between short click and a long click
int button_state = 0; //0= none, 1= a click was stated, 2=still short click, 3= starting long click, 4=still long click, 5= end of a click.
int button_id = 0; //0=mode button, 1=button1, ...
int hand_mode = 0 ; // 0 = long click modes, 1 = mode1, 2 = mode2, ...
unsigned long t_press; // the time when a button press was strated

// battery function - parameters and declaration:
#define DT_BATTERY_STATUS  (10 * 60 * 1000) //check battery every 10 min
#define BATTERY_MIN 1400  //=~6v , 385 esp unit =~1v for ADC_11db and voltage devider of 1/3
#define BATTERY_MAX 1800  //=~8.4v
unsigned long t_check_battery; //the elapsed time between battery status checks
uint8_t battery_level = 100; // battery status in [%]

// declaring config parameters:
int thr_value_L;
int thr_value_H;
int t_start;
int win_width; //prefered 2^x
int thr_slope_L;
int thr_slope_H;
int thr_factor[MOTORS_NUM+1];
unsigned char dv_config;
bool is_debug = false;

unsigned char all_config[CONFIG_NUM+1]; 
int config_id = 0;

// default values for config parameters:
// These parameters are the default values saved on the controller memeory
#define THR_VALUE_L 20  // [CURRENT_UNIT] current threshold value for LOW torque level
#define THR_VALUE_H 80  // [CURRENT_UNIT] current threshold value for HIGH torque level
#define T_START     150  // [msec] The time it takes to the initial high starting current to get back to normal
#define WIN_WIDTH   20  // [units] window width of the moving average filter
#define THR_SLOPE_L 10  //  [CURRENT_UNIT] the time [msec] threshold for increasing current for LOW torque level
#define THR_SLOPE_H 20  //  [CURRENT_UNIT] the time [msec] threshold for increasing current for LOW torque level
#define THR_FACTOR0 100  // [units] The multiplaction factor for the Wrist motor Thrshold values
#define THR_FACTOR1 150  // [units] The multiplaction factor for Finger1 motor Thrshold values
#define THR_FACTOR2 150  // [units] The multiplaction factor for Finger2 motor Thrshold values
#define THR_FACTOR3 100  // [units] The multiplaction factor for Finger3 motor Thrshold values
#define THR_FACTOR4 100  // [units] The multiplaction factor for Finger4 motor Thrshold values
#define DV_CONFIG   2  // [units] CURRENT_UNIT * DV_CONFIG = esp unit which is measured by the controller 
#define IS_DEBUG    0  // [bool] 0 - no debug mode, reduced comments, 1 - debug mode

const unsigned char all_config_default[CONFIG_NUM+1] = {THR_VALUE_L,THR_VALUE_H,T_START,WIN_WIDTH,THR_SLOPE_L,THR_SLOPE_H,
                                                         THR_FACTOR0,THR_FACTOR1,THR_FACTOR2,THR_FACTOR3,THR_FACTOR4,
                                                        DV_CONFIG,IS_DEBUG};
                                                        
// declaring BLE variables: all presentes
unsigned char current_preset[MAX_PRESET_BYTES];
unsigned char preset1[MAX_PRESET_BYTES];
unsigned char preset2[MAX_PRESET_BYTES];
unsigned char preset3[MAX_PRESET_BYTES];
unsigned char preset4[MAX_PRESET_BYTES];
unsigned char preset5[MAX_PRESET_BYTES];
unsigned char preset6[MAX_PRESET_BYTES];
unsigned char preset7[MAX_PRESET_BYTES];
unsigned char preset8[MAX_PRESET_BYTES];
unsigned char preset9[MAX_PRESET_BYTES];
unsigned char preset10[MAX_PRESET_BYTES];
unsigned char preset11[MAX_PRESET_BYTES];
unsigned char preset12[MAX_PRESET_BYTES];

unsigned char* all_presets[PRESETS_NUM+1]= {preset1,preset2,preset3,preset4,preset5,
                                            preset6,preset7,preset8,preset9,preset10,
                                            preset11,preset12,current_preset};

// default values:
// each preset is defined as following:
// movement length byte, torque,time[TIME_UNIT=50msec],active motor, motor direction
#define CLOSE_ALL_HIGH_TORQUE {5, 0b11111000, 20, 0b01111000, 0b11111000} 
#define OPEN_ALL              {5, 0b11111000, 20, 0b01111000, 0b00000000}
#define CLOSE_ALL_LOW_TORQUE  {5, 0b00000000, 20, 0b01111000, 0b11111000}
#define TRIPOD                {5, 0b00000000, 20, 0b01111000, 0b11100000}
#define TRIPOD_HIGH           {5, 0b11111000, 20, 0b01111000, 0b11100000}
#define PINCH                 {5, 0b00000000, 20, 0b01111000, 0b10100000}
#define PINCH_HIGH            {5, 0b11111000, 20, 0b01111000, 0b10100000}
#define POINTER               {5, 0b00000000, 20, 0b01111000, 0b10111000}
#define COOL                  {5, 0b00000000, 20, 0b01111000, 0b10110000}
#define THE_FINGER            {5, 0b00000000, 20, 0b01111000, 0b11011000}
#define TURN_RIGHT            {5, 0b00000000, 25, 0b10000000, 0b10110000}
#define TURN_LEFT             {5, 0b00000000, 25, 0b10000000, 0b00110000}

const unsigned char all_presets_default[PRESETS_NUM+1][ACTION_BYTES+1+1] = {CLOSE_ALL_HIGH_TORQUE,OPEN_ALL,CLOSE_ALL_LOW_TORQUE,
                                                           TRIPOD,TRIPOD_HIGH,PINCH,PINCH_HIGH,POINTER,COOL,
                                                           THE_FINGER,TURN_RIGHT,TURN_LEFT};
// initialize communication parameters:
int current_task = 0;
int current_preset_id = 0;
bool was_connected = false;

/*************************************************************************************/
/*                  BLE Class Definition and Set Callbacks:                          */
/*************************************************************************************/
// All BLE characteristic UUIDs are of the form:
// 0000XXXX-0000-1000-8000-00805f9b34fb

#define HAND_DIRECT_EXECUTE_SERVICE_UUID     "e0198000-7544-42c1-0000-b24344b6aa70"
#define EXECUTE_ON_WRITE_CHARACTERISTIC_UUID "e0198000-7544-42c1-0001-b24344b6aa70"

#define HAND_PRESET_SERVICE_UUID             "e0198001-7544-42c1-0000-b24344b6aa70"

#define HAND_TRIGGER_SERVICE_UUID            "e0198002-7544-42c1-0000-b24344b6aa70"
#define TRIGGER_ON_WRITE_CHARACTERISTIC_UUID "e0198002-7544-42c1-0001-b24344b6aa70"
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

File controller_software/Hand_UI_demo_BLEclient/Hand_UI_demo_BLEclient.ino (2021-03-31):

/*
 * This code is a demo code for any wireless system which translates the user's desires 
 * into hand movements. This code allows you to control the Oded Hand - a low cost, open 
 * source prosthetic hand that anyone can build (https://github.com/Haifa3D) via BLE 
 * protocl we developed for this pupose (For more information about the BLE protocol see 
 * https://github.com/Haifa3D/haifa3d-hand-app/blob/master/Protocol.md) 
 * 
 * In general, the Hand itself is the server and you UI system is the client.
 * Here we show how to communicate with the hand using esp32 controller, and
 * go to sleep if no connection was established
 * 
 * Getting started (for ESP32-based system): 
 * add your device address (under "BlE Parameters ")
 * add your system parameters - HW and SW (under "Your System Setting")
 * add in the "setup loop" your system setup code.
 * add your system functions (under "Your System Functions")
 * 
 * now you need to decide how to communicate with the hand - you can use
 * the 'Execute Characteristic' (i.e. pRemoteCharExecute) and/or the 'Trigger 
 * Characteristic' (i.e. pRemoteCharTrigger).
 * For pRemoteCharExecute: 
 *      unsigned char msg =  {5, 0b11111000, 20, 0b01111000, 0b00000000}; //movement length byte,torque,time,active motor, motor direction 
        pRemoteCharExecute->writeValue(msg,msg[0]);
 *      (for more detail see our BLE protocol at the link above)
 * For pRemoteCharTrigger: 
 *      uint8_t preset_id = 0;  //can be 0-11 since we have 12 defined presets in the Oded Hand
        pRemoteCharTrigger->writeValue(&preset_id,1);
        (to define your presets check out our mobile app: https://play.google.com/store/apps/details?id=com.gjung.haifa3d)
 *
 * Here you can see our system demo for a LegSwitch - the switch is conncted to GPIO 4.
 * If the switch has pressed two short and successive times the system triggers 'preset 0' (which we defined in the app as close all fingers)
 * If the switch has pressed three times the system sends an open task via the 'Execute Characteristic'.
 * 
 */

 /***********************************************************/
/*                Libraries                                */
/***********************************************************/
#include <BLEDevice.h>
#include <BLEAdvertisedDevice.h>

/*************************************************************************************/
/*                                  BlE Parameters                                   */
/*************************************************************************************/
#define MY_DEVICE_ADDRESS  "24:62:ab:f2:af:46" // add here you devicec address

#define HAND_DIRECT_EXECUTE_SERVICE_UUID     "e0198000-7544-42c1-0000-b24344b6aa70"
#define EXECUTE_ON_WRITE_CHARACTERISTIC_UUID "e0198000-7544-42c1-0001-b24344b6aa70"

#define HAND_TRIGGER_SERVICE_UUID            "e0198002-7544-42c1-0000-b24344b6aa70"
#define TRIGGER_ON_WRITE_CHARACTERISTIC_UUID "e0198002-7544-42c1-0001-b24344b6aa70"

static BLEUUID serviceExeUUID(HAND_DIRECT_EXECUTE_SERVICE_UUID);// The remote service we wish to connect to.
static BLEUUID    charExeUUID(EXECUTE_ON_WRITE_CHARACTERISTIC_UUID);// The characteristic of the remote service we are interested in - execute.
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

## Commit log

2021-09-07 update battery check function
2024-08-31 Change license to Non-Profit Open Software License (“Non-Profit OSL”) 3.0
